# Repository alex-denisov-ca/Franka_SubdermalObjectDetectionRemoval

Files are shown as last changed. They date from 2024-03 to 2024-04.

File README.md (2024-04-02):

# Robot-assisted Subdermal Foreign Object Detection and Removal For Franka Panda

## **Quick Start Guide**
This project is for use with the Franka Emika Panda cobot and the Healson C30L ultrasound probe, as well as similar probes and cobots.

The project uses the Franka robot alongside an ultrasound probe to scan a section of ultrasound gel or water; the medium will mimic human flesh. Within the medium, one or more metallic bolts or other objects will simulate shrapnel subdermally embedded. 

*(0): Startup*<br />
Git clone and build the project, specifically the csc496 directory of the project in the same directory that contains the Franka Panda's [libfranka](https://github.com/frankaemika/libfranka) directory.

Connect to the Franka control interface and ensure everything is properly initialized; joints are unlocked, and the robot is not reflex-locked or user-stopped.
First, set the z component of the end effector to 150mm in Franka Desk, also measure and set the weight of the Franka hand including the probe, grippers and holders (print and user depedant).
Second, enable the [FCI](https://frankaemika.github.io/docs/getting_started.html)

Install printed hardware to the Franka hand, seal important electrical components on and around the robot, set your tray/working area, then fill the tray with the preferred medium and insert foreign bodies.

Then start the docker container included in the "docker" directory within "csc496":
    run build_docker_container.sh
    run start_docker_container.sh
    run open_docker_terminal.sh
    to close the running terminal, run stop_docker_container.sh

*(1): Running the code*<br />
Inside the docker container, go to `/root/git/scratchpad/csc496/build` and run `rm CMakeCache.txt && cmake ../ && make` in the bash terminal.
then run `run.sh` in the terminal; this script links all the steps together onto a single terminal, follow instructions and prompts that show up on the terminal.
    There will be four distinct steps, with an "operator" sitting at the terminal and the ultrasound screen and a "guide" watching the robot and manning the enabling device.

    (0): Setting the origin of the scanner
        - The guide will move the probe to the bottom left of the tray farthest away from the robot
           and to the side that it has its power ports.

    (1): Rough scanning mode
        - the probe will begin scanning the working area, the operator should press space 
          when an anomaly is detected.

    (2): Keyboard guidance mode
        - The operator will have to navigate to the rough position and center the object on the ultrasound, 
          this should be done with the help of the guide to avoid collisions.

    (2.5): (Suggested) Remove the ultrasound probe from the holder.      

    (3): Object Retrieval
        - after the operator has identified the object then, the robot will attempt to grasp the object, 
          upon completion, it will home and drop the object for the guide to catch upon operator approval. 

## **Running Details**
if, for some reason, you don't use `run.sh`, then you can run each step individually after following the initial instructions from Startup, as shown below:<br />

*(0): Set origin of scan*<br />
     - sets and records the origin of scanning sequence<br />
     - use for manually running scan from origin<br />

    Run manually:
        ./set_origin <YOUR_FRANKA_IP>

    Controls:
        Enter - saves the position
        Any other key - quit the program

*(1): Automated scanning of the medium in a rectangular pattern*<br />
     - when the operator sees a foreign object on the ultrasound screen they press the space bar<br />
     - the location is saved in a text file for further inspection and adjustment<br />
     - this simulates scanning a large portion of the body to locate multiple pieces of shrapenal<br />

    Run manually:
        ./run_autoscan_rough_capture <YOUR_FRANKA_IP> <Origin X> <Origin Y> <Origin Z>

    Controls:
        Space - saves the position

*(2): Fine position finding* <br />
     - Now that you know the approximate position of the shrapnel, use the keyboard to locate it <br />
     - Once the operator has found the center of the object, they will press 'space' and save the coordinates <br />
     - The saved coordinates will also be saved to a text file; both to handle multiple pieces of shrapnel, or multiple grasping attempts of the same object <br />
    
    Run:
        ./run_keyboard_input_capture <YOUR_FRANKA_IP>  <X> <Y> <Z>

     Controls:
        W - moves forward (towards the robots base)
        A - moves left (towards the side of the robots power connectors)
        S - moves backward (away from the robots base)
        D - moves right (towards the side of the robots ethernet port)
        Space - saves the position
        R - moves upwards
        F - move downwards
        T - releases/opens the gripper
        G - closes gripper to grasp
        Escape - stops and closes the program

*(3): Object extraction*<br />
     - The user will be prompted for a raw x,y position<br />
     - The operator will enter the x,y positions determined from the previous step<br />
     - The robot will then automatically go to its home position, open the gripper, go to the object, close the gripper, and extract it<br />
     - If the robot fails to grasp and extract the object, repeat step 2 or use alternative object positions already collected in the previous step<br />
     - Press the space bar to open the gripper and drop the extracted object (or simply open the gripper for another iteration)<br />
  
    Run manually:
        ./grasp_given_xyz <YOUR_FRANKA_IP>  <X> <Y> <Z> 
        
    Inputs:
        x position - raw x position of ultrasound detected object
        y position - raw y position of ultrasound detected object

     Controls:
        Enter - On prompt, continue execution of the next task
        Space - On prompt, open the gripper

## **Hardware and Envrionment**
For hardware used in the project, go to the "Models" directory and see [Hardware_Instructions.pdf](https://github.com/alex-denisov-ca/Franka_SubdermalObjectDetectionRemoval/blob/main/Models/Hardware_Instructions.pdf) for printing and assembly information.

Once assembled, there is a distance of 150mm from the flange of the robot to the ends of the grippers; set these values in Franka Desk.
It should also be noted that the center of the ultrasound probe is 60mm away from the center of the end-effector; 
with any tray or working area, there are mechanical limitations that result in spaces where the probe cannot scan / the grippers cannot reach.

It is suggested to use an ultrasound gel for running this project; for best results, smooth the gel before every run (this can be done with something unimportant, like a student ID).

For running in custom environments, you will also have to measure dimensions and the coordinate of your working space; `set_origin` allows you to move the board anywhere in the working space (without rotations), but it may be necessary to manually tweak code if your tray is larger or smaller than the one provided to work with the auto scan feature.

## **Dependencies**
All files are to be run on a Linux real-time kernel.
The github repo OR the csc496 directory included in the repo must be in the same directory as [libfranka](https://github.com/frankaemika/libfranka); i.e in some directory X, there will X/libfranka, X/csc496, X/Models, etc.

If you are NOT running the provided docker container, you will have to have at minimum [ncurses-6.0](https://lists.gnu.org/archive/html/info-gnu/2015-08/msg00002.html) installed; 

## **Citation**
This codebase is modified from the one provided in CSC496H5 at the University of Toronto Mississauga, taught by Professor Lueder Kahrs and provided by Ruthrash Hari; based on the Franka Emika [libfranka repo.](https://github.com/frankaemika/libfranka)

Citation is available in the About section of the GitHub project or the CITATION.cff file.

## **Testing**
We have tested this repo using the Franka Panda robot, the Healson C30L ultrasound probe, and all stl files provided in this repository. Tests have been running on multiple robots; different robots have different vertical offsets from their base due to mounting variances, and thus, some board parameters need to be tweaked between robots.

When testing, running for the first time, or tweaking the parameters, it is important to always have one person manning the enabling device and developing incrementally with one change at a time. For example, changing the speed; start at a known working speed, then increment it to the desired value, etc.

In testing the code, it is best to perform the tests without a medium inside the tray. We have tested each of the four sections above individually and together with `run.sh`. 

We have run through all steps of the project multiple times using a 15mm M6 screw (shrapnel) embedded in ultrasound gel (medium), resulting in successful objection detection at all stages and removal from the medium. 

Our set_origin code works at any point in the working space; it simply records the x,y, and z components of the gripper and saves them to a text file.

We ran our rough scanning code with the tray affixed at different positions on two robots; the scanning code given the set_origin program will adapt to the z offset and work with multiple volumes of the medium. 

We ran keyboard extraction in many envrioments, it may fail if the operator runs the gripper into the wall fo the tray or another rigid object, fine tuning for different application is possible by setting how much the gripper moves on each keypress.

We varied the placement of the shrapnel inside the medium, within the mechanial boundaries of the gripper and where successful in extracting the bolt; the bolt was succesfully picked up in both the laying down and  upright position. Although, some orentiations are untested, such as the bolt laying at a 45 degree angle; making it hard to pick up and easily slide away from the gripper jaws. 

If the program is unsuccessful, there may be times that the terminal running the program will freeze to an orphan thread run by one of the members. It is also important to move the robot between runs to ensure there is no reflex-lock and also to not put excessive force on the robot while it's moving and running.

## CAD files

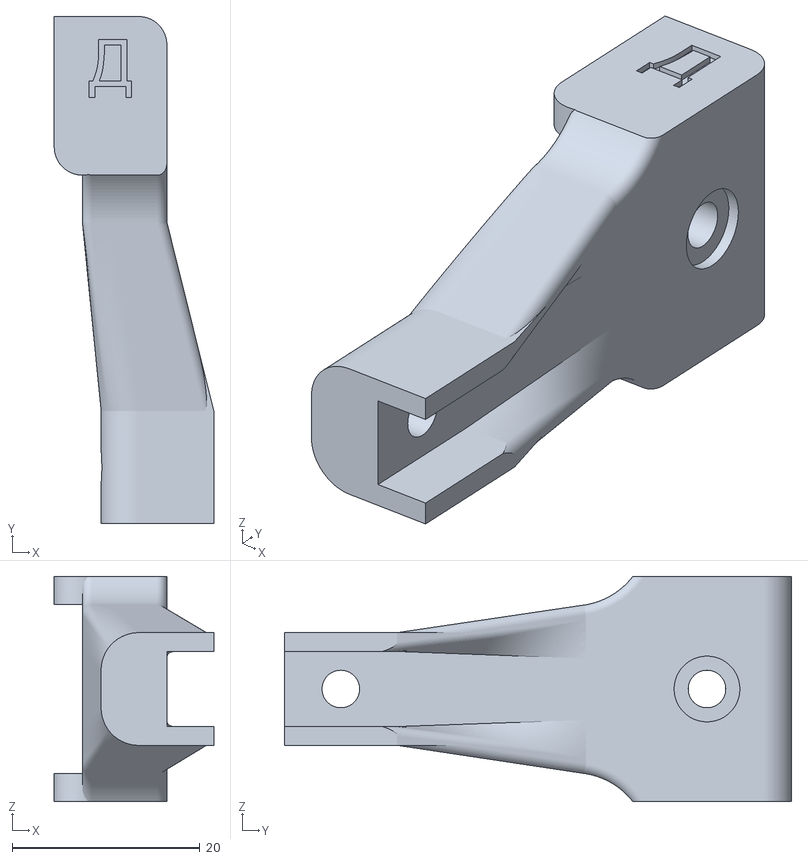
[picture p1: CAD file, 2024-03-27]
Models/Franka_gripper.stl
17.0 x 54.0 x 24.0

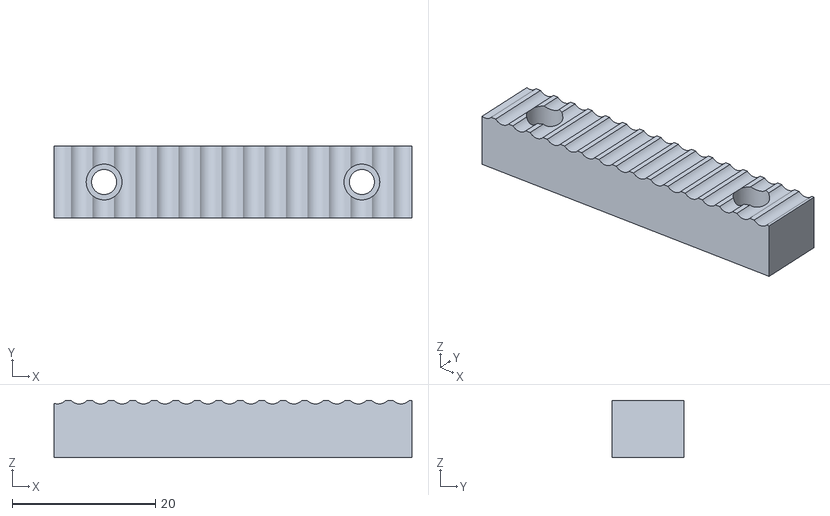
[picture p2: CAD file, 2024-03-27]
Models/Franka_probe_clamp_softjaw.stl
50.0 x 10.0 x 8.00

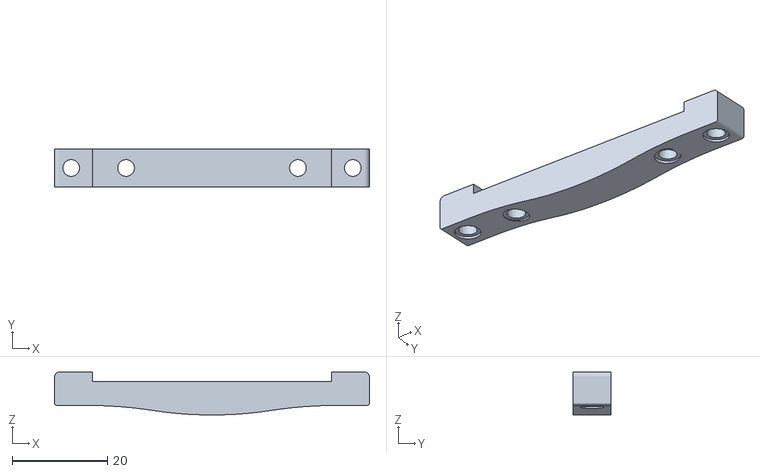
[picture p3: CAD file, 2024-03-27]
Models/Franka_probe_clamp.stl
66.0 x 8.00 x 9.00

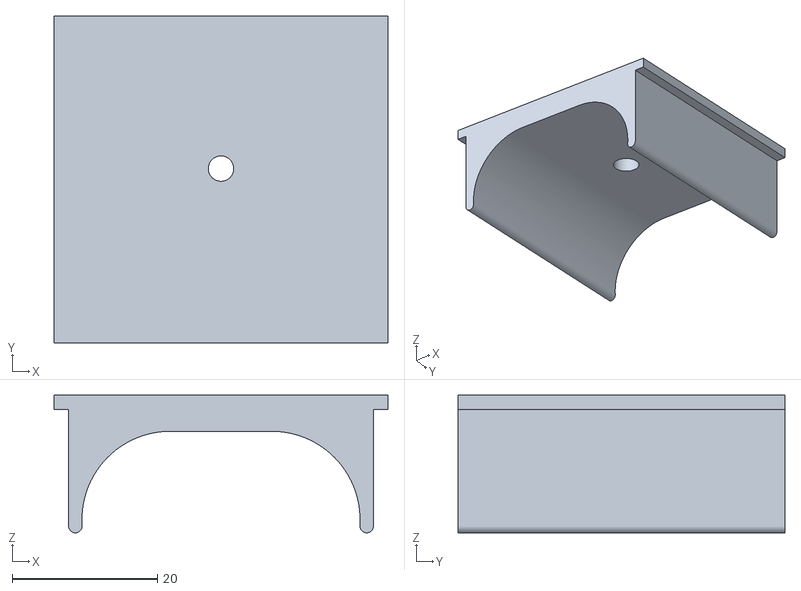
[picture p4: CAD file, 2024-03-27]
Models/Franka_probe_holder_softjaw.stl
46.0 x 45.0 x 19.0

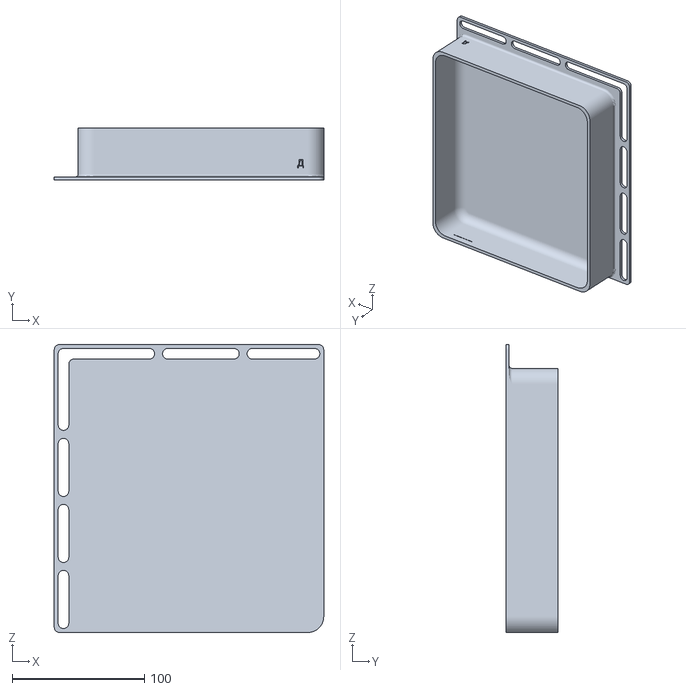
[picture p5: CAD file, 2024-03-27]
Models/Tray_surgery_mock.stl
204.0 x 39.5 x 218.0

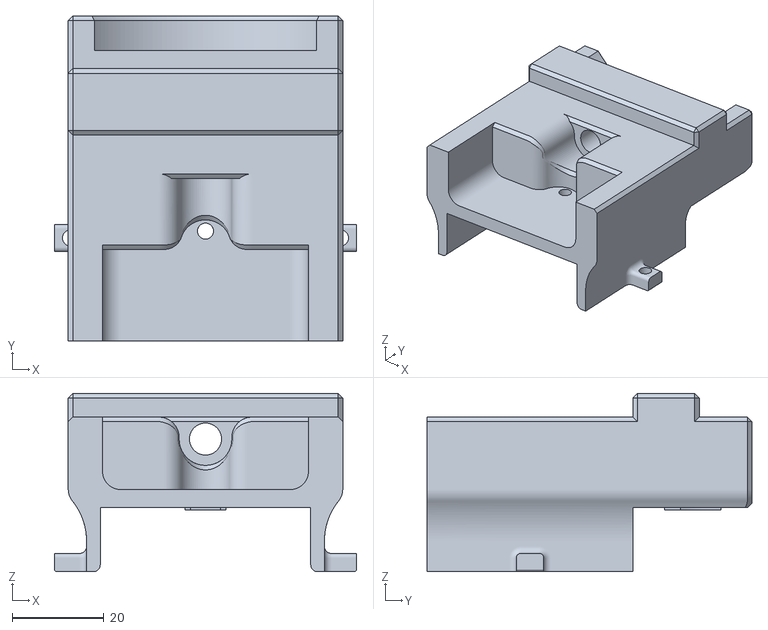
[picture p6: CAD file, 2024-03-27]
Models/Franka_probe_holder.stl
66.0 x 71.0 x 39.0

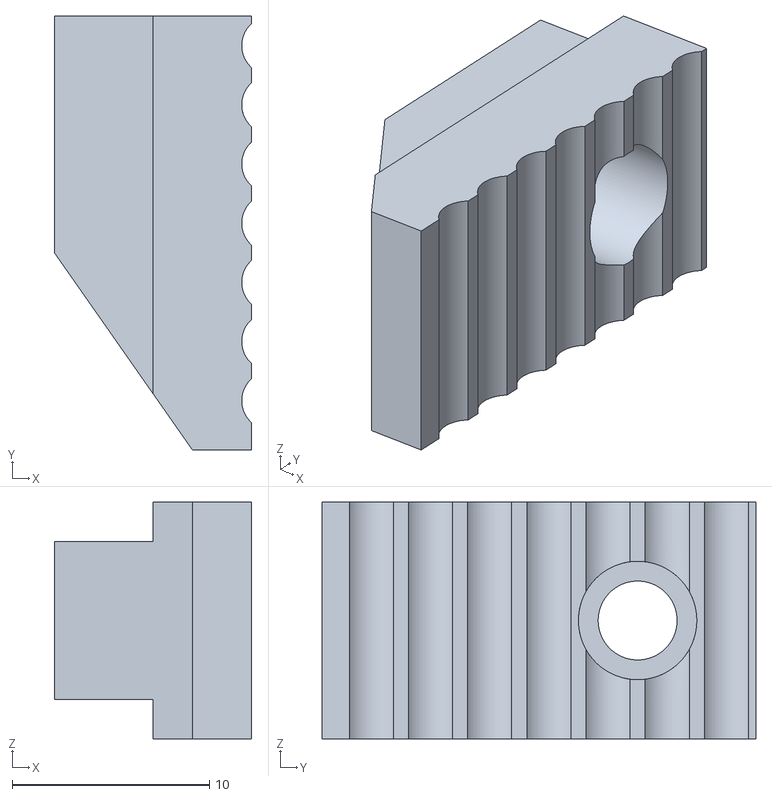
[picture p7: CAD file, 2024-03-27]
Models/Franka_gripper_softjaw.stl
10.0 x 22.0 x 12.0

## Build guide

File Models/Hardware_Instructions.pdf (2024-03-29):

Hardware and 3D Printing Documentation Robot-assisted Subdermal Foreign Object Detection and Removal For Franka Emika Panda & Similar Robots Required Hardware:
1x M6 Bolt - 40mm: attachment of the ultrasound holder to the Franka hand
3x (Optional) M6 Bolt - 10mm: tray fastening depends on mounting surface and tray used

2x M3 Bolt - 45mm: attachment of the clamp to the holder
2x M3 Bolt - 20mm: attachment of the grippers to the end-effector
5x M3 Bolt - 12mm: attachment of malleable materials to rigid bodies

7x M3 Nuts
6x M3 Thumb Nuts - 12x4mm

Printing Instructions:
Objects shown in light green are to be printed in PLA or another suitable material; it is preferable to use tree supports and print with four walls and 20-35 percent infill, depending on the material.

Objects shown in light blue from left to right are Franka_probe_holder.stl, Franka_probe_holder.stl, and (2x) Franka_gripper.stl

Objects shown in yellow/gray stripes are to be printed in a malleable material such as TPU with any shore hardness; preferably print with a brim, no supports, four walls and use Cross3D or similar deformation-compliant infill pattern at 10-25 percent infill.

Objects shown in striped yellow/gray from left to right are: Franka_probe_softjaw.stl, Franka_probe_holder_softjaw.stl and (2x) Franka_gripper_softjaw.stl

Below is the suggested printed orientation for each object:

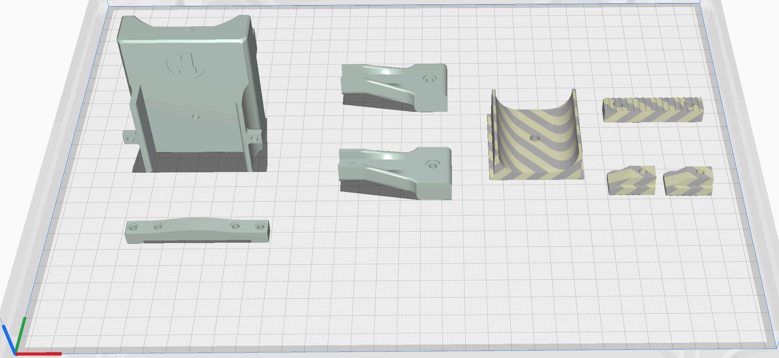
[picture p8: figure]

For Franka Emika Panda & Similar Robots

You may use the tray provided as Tray_surgery_mock.stl to hold ultrasound gel/liquid for the surgery mock; any other rigid pan or tray will also work, but it must be fastened and waterproofed correctly.

The figure below shows the orientation for printing Tray_surgery_mock.stl; use an attachment glue as large flat square objects will warp when cooling for most materials. Print in PLA or another suitable material; no supports are needed, and print with six walls and 20-35 percent infill, depending on the material. Use as large of a skirt as possible when printing.

The Tray used in this project is quite large and may not be suitable for all users depending on printer limitations; users should scale the mock or use an alternative method to hold the gel/water and shrapnel.

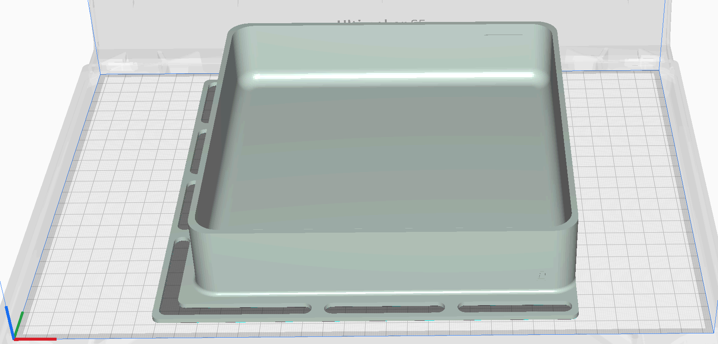
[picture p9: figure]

Assembly:
Use 12mm M3 bolts to attach all TPU parts to rigid parts, with bolts.
Use the 20mm M3 bolts and the thumb screws to attach the grippers to the flange extenders.
Use the 45mm M3 bolts to attach the clamp to the ultrasound holder, alongside two bolts and four thumb screws.
Use the 40mm M6 bolt to attach the probe holder to the Franka Panda robot.

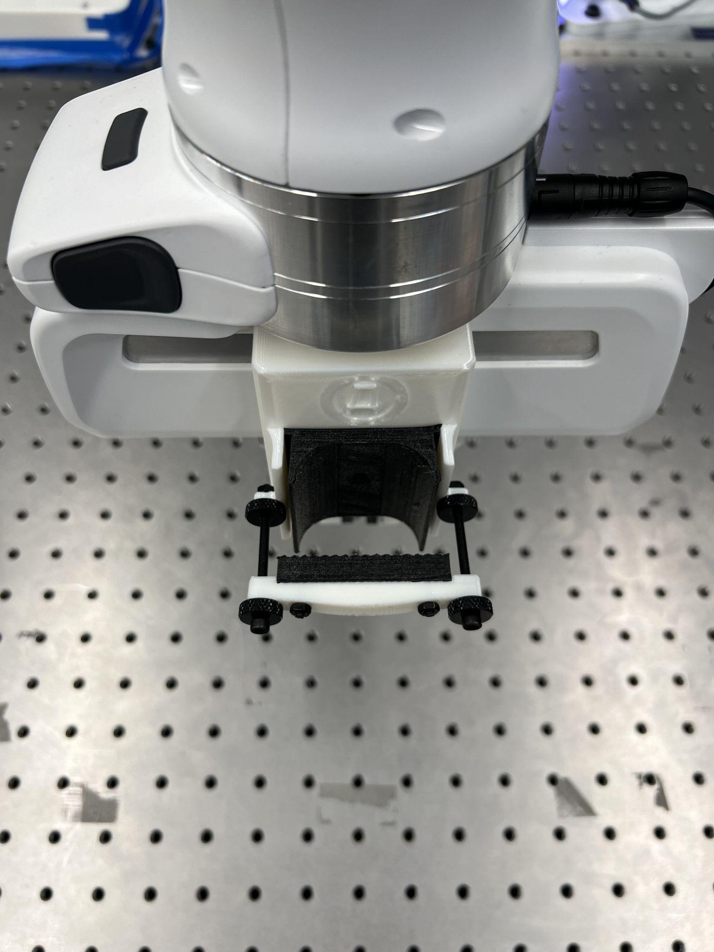
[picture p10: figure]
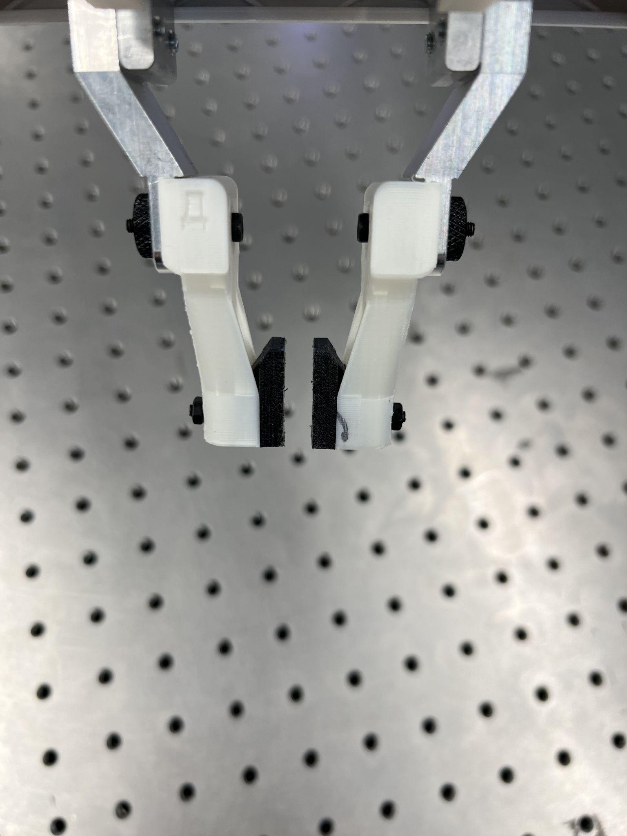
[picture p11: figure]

For Franka Emika Panda & Similar Robots

Photos of assembled components are provided below:

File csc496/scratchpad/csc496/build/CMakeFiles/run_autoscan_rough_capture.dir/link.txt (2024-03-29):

/usr/bin/c++     CMakeFiles/run_autoscan_rough_capture.dir/runners/autoscan_rough_capture.cpp.o CMakeFiles/run_autoscan_rough_capture.dir/src/common.cpp.o CMakeFiles/run_autoscan_rough_capture.dir/src/ik.cpp.o CMakeFiles/run_autoscan_rough_capture.dir/src/teleop/follower.cpp.o CMakeFiles/run_autoscan_rough_capture.dir/src/teleop/leader.cpp.o CMakeFiles/run_autoscan_rough_capture.dir/src/teleop/network_client.cpp.o CMakeFiles/run_autoscan_rough_capture.dir/src/teleop/network_server.cpp.o  -o run_autoscan_rough_capture   -L/usr/local/include  -Wl,-rpath,/usr/local/include:/usr/local/lib /usr/local/lib/libfranka.so.0.9.2 /usr/lib/x86_64-linux-gnu/libboost_system.so.1.71.0 /usr/lib/x86_64-linux-gnu/libboost_thread.so.1.71.0 /usr/lib/x86_64-linux-gnu/libPocoFoundation.so.62 -lcurses /usr/lib/x86_64-linux-gnu/libform.so -lpthread -ldl -lrt /usr/lib/x86_64-linux-gnu/libpcre.so /usr/lib/x86_64-linux-gnu/libz.so /usr/lib/x86_64-linux-gnu/libboost_atomic.so.1.71.0 -pthread

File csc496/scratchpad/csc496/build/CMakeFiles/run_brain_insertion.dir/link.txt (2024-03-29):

/usr/bin/c++     CMakeFiles/run_brain_insertion.dir/runners/brain_insertion.cpp.o CMakeFiles/run_brain_insertion.dir/src/common.cpp.o CMakeFiles/run_brain_insertion.dir/src/ik.cpp.o CMakeFiles/run_brain_insertion.dir/src/teleop/follower.cpp.o CMakeFiles/run_brain_insertion.dir/src/teleop/leader.cpp.o CMakeFiles/run_brain_insertion.dir/src/teleop/network_client.cpp.o CMakeFiles/run_brain_insertion.dir/src/teleop/network_server.cpp.o  -o run_brain_insertion   -L/usr/local/include  -Wl,-rpath,/usr/local/include:/usr/local/lib /usr/local/lib/libfranka.so.0.9.2 /usr/lib/x86_64-linux-gnu/libboost_system.so.1.71.0 /usr/lib/x86_64-linux-gnu/libboost_thread.so.1.71.0 /usr/lib/x86_64-linux-gnu/libPocoFoundation.so.62 -lpthread -ldl -lrt /usr/lib/x86_64-linux-gnu/libpcre.so /usr/lib/x86_64-linux-gnu/libz.so /usr/lib/x86_64-linux-gnu/libboost_atomic.so.1.71.0 -pthread

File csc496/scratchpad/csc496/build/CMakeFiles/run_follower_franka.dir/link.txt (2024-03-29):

/usr/bin/c++     CMakeFiles/run_follower_franka.dir/runners/teleop/follower_franka.cpp.o  -o run_follower_franka   -L/usr/local/include  -Wl,-rpath,/usr/local/include:/usr/local/lib libfollower.a libnetwork_server.a libfranka_common.a libik.a /usr/local/lib/libfranka.so.0.9.2 /usr/lib/x86_64-linux-gnu/libboost_system.so.1.71.0 /usr/lib/x86_64-linux-gnu/libboost_thread.so.1.71.0 /usr/lib/x86_64-linux-gnu/libboost_atomic.so.1.71.0 -pthread

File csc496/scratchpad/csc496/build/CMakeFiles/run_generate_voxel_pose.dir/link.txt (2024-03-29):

/usr/bin/c++     CMakeFiles/run_generate_voxel_pose.dir/runners/generate_voxel_pose.cpp.o CMakeFiles/run_generate_voxel_pose.dir/src/common.cpp.o CMakeFiles/run_generate_voxel_pose.dir/src/ik.cpp.o CMakeFiles/run_generate_voxel_pose.dir/src/teleop/follower.cpp.o CMakeFiles/run_generate_voxel_pose.dir/src/teleop/leader.cpp.o CMakeFiles/run_generate_voxel_pose.dir/src/teleop/network_client.cpp.o CMakeFiles/run_generate_voxel_pose.dir/src/teleop/network_server.cpp.o  -o run_generate_voxel_pose   -L/usr/local/include  -Wl,-rpath,/usr/local/include:/usr/local/lib /usr/local/lib/libfranka.so.0.9.2 /usr/lib/x86_64-linux-gnu/libboost_system.so.1.71.0 /usr/lib/x86_64-linux-gnu/libboost_thread.so.1.71.0 /usr/lib/x86_64-linux-gnu/libPocoFoundation.so.62 -lpthread -ldl -lrt /usr/lib/x86_64-linux-gnu/libpcre.so /usr/lib/x86_64-linux-gnu/libz.so /usr/lib/x86_64-linux-gnu/libboost_atomic.so.1.71.0 -pthread

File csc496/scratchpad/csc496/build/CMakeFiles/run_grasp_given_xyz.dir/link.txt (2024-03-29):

/usr/bin/c++     CMakeFiles/run_grasp_given_xyz.dir/runners/grasp_given_xyz.cpp.o CMakeFiles/run_grasp_given_xyz.dir/src/common.cpp.o CMakeFiles/run_grasp_given_xyz.dir/src/ik.cpp.o CMakeFiles/run_grasp_given_xyz.dir/src/teleop/follower.cpp.o CMakeFiles/run_grasp_given_xyz.dir/src/teleop/leader.cpp.o CMakeFiles/run_grasp_given_xyz.dir/src/teleop/network_client.cpp.o CMakeFiles/run_grasp_given_xyz.dir/src/teleop/network_server.cpp.o  -o run_grasp_given_xyz   -L/usr/local/include  -Wl,-rpath,/usr/local/include:/usr/local/lib /usr/local/lib/libfranka.so.0.9.2 /usr/lib/x86_64-linux-gnu/libboost_system.so.1.71.0 /usr/lib/x86_64-linux-gnu/libboost_thread.so.1.71.0 /usr/lib/x86_64-linux-gnu/libPocoFoundation.so.62 -lcurses /usr/lib/x86_64-linux-gnu/libform.so -lpthread -ldl -lrt /usr/lib/x86_64-linux-gnu/libpcre.so /usr/lib/x86_64-linux-gnu/libz.so /usr/lib/x86_64-linux-gnu/libboost_atomic.so.1.71.0 -pthread

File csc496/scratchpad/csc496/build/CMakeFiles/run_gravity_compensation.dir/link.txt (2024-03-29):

/usr/bin/c++     CMakeFiles/run_gravity_compensation.dir/runners/gravity_compensation.cpp.o CMakeFiles/run_gravity_compensation.dir/src/common.cpp.o CMakeFiles/run_gravity_compensation.dir/src/ik.cpp.o CMakeFiles/run_gravity_compensation.dir/src/teleop/follower.cpp.o CMakeFiles/run_gravity_compensation.dir/src/teleop/leader.cpp.o CMakeFiles/run_gravity_compensation.dir/src/teleop/network_client.cpp.o CMakeFiles/run_gravity_compensation.dir/src/teleop/network_server.cpp.o  -o run_gravity_compensation   -L/usr/local/include  -Wl,-rpath,/usr/local/include:/usr/local/lib /usr/local/lib/libfranka.so.0.9.2 /usr/lib/x86_64-linux-gnu/libboost_system.so.1.71.0 /usr/lib/x86_64-linux-gnu/libboost_thread.so.1.71.0 /usr/lib/x86_64-linux-gnu/libPocoFoundation.so.62 -lpthread -ldl -lrt /usr/lib/x86_64-linux-gnu/libpcre.so /usr/lib/x86_64-linux-gnu/libz.so /usr/lib/x86_64-linux-gnu/libboost_atomic.so.1.71.0 -pthread

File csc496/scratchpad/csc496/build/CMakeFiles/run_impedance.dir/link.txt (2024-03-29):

/usr/bin/c++     CMakeFiles/run_impedance.dir/runners/impedance.cpp.o CMakeFiles/run_impedance.dir/src/common.cpp.o CMakeFiles/run_impedance.dir/src/ik.cpp.o CMakeFiles/run_impedance.dir/src/teleop/follower.cpp.o CMakeFiles/run_impedance.dir/src/teleop/leader.cpp.o CMakeFiles/run_impedance.dir/src/teleop/network_client.cpp.o CMakeFiles/run_impedance.dir/src/teleop/network_server.cpp.o  -o run_impedance   -L/usr/local/include  -Wl,-rpath,/usr/local/include:/usr/local/lib /usr/local/lib/libfranka.so.0.9.2 /usr/lib/x86_64-linux-gnu/libboost_system.so.1.71.0 /usr/lib/x86_64-linux-gnu/libboost_thread.so.1.71.0 /usr/lib/x86_64-linux-gnu/libPocoFoundation.so.62 -lpthread -ldl -lrt /usr/lib/x86_64-linux-gnu/libpcre.so /usr/lib/x86_64-linux-gnu/libz.so /usr/lib/x86_64-linux-gnu/libboost_atomic.so.1.71.0 -pthread

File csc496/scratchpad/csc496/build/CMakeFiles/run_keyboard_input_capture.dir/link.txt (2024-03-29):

/usr/bin/c++     CMakeFiles/run_keyboard_input_capture.dir/runners/keyboard_input_capture.cpp.o CMakeFiles/run_keyboard_input_capture.dir/src/common.cpp.o CMakeFiles/run_keyboard_input_capture.dir/src/ik.cpp.o CMakeFiles/run_keyboard_input_capture.dir/src/teleop/follower.cpp.o CMakeFiles/run_keyboard_input_capture.dir/src/teleop/leader.cpp.o CMakeFiles/run_keyboard_input_capture.dir/src/teleop/network_client.cpp.o CMakeFiles/run_keyboard_input_capture.dir/src/teleop/network_server.cpp.o  -o run_keyboard_input_capture   -L/usr/local/include  -Wl,-rpath,/usr/local/include:/usr/local/lib /usr/local/lib/libfranka.so.0.9.2 /usr/lib/x86_64-linux-gnu/libboost_system.so.1.71.0 /usr/lib/x86_64-linux-gnu/libboost_thread.so.1.71.0 /usr/lib/x86_64-linux-gnu/libPocoFoundation.so.62 -lcurses /usr/lib/x86_64-linux-gnu/libform.so -lpthread -ldl -lrt /usr/lib/x86_64-linux-gnu/libpcre.so /usr/lib/x86_64-linux-gnu/libz.so /usr/lib/x86_64-linux-gnu/libboost_atomic.so.1.71.0 -pthread

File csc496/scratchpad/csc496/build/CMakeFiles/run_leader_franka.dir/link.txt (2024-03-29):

/usr/bin/c++     CMakeFiles/run_leader_franka.dir/runners/teleop/leader_franka.cpp.o  -o run_leader_franka   -L/usr/local/include  -Wl,-rpath,/usr/local/include:/usr/local/lib libleader.a libnetwork_client.a libfranka_common.a /usr/local/lib/libfranka.so.0.9.2 /usr/lib/x86_64-linux-gnu/libboost_system.so.1.71.0 /usr/lib/x86_64-linux-gnu/libboost_thread.so.1.71.0 /usr/lib/x86_64-linux-gnu/libboost_atomic.so.1.71.0 -pthread

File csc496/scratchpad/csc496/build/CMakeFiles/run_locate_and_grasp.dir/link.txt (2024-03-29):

/usr/bin/c++     CMakeFiles/run_locate_and_grasp.dir/runners/locate_and_grasp.cpp.o CMakeFiles/run_locate_and_grasp.dir/src/common.cpp.o CMakeFiles/run_locate_and_grasp.dir/src/ik.cpp.o CMakeFiles/run_locate_and_grasp.dir/src/teleop/follower.cpp.o CMakeFiles/run_locate_and_grasp.dir/src/teleop/leader.cpp.o CMakeFiles/run_locate_and_grasp.dir/src/teleop/network_client.cpp.o CMakeFiles/run_locate_and_grasp.dir/src/teleop/network_server.cpp.o  -o run_locate_and_grasp   -L/usr/local/include  -Wl,-rpath,/usr/local/include:/usr/local/lib /usr/local/lib/libfranka.so.0.9.2 /usr/lib/x86_64-linux-gnu/libboost_system.so.1.71.0 /usr/lib/x86_64-linux-gnu/libboost_thread.so.1.71.0 /usr/lib/x86_64-linux-gnu/libPocoFoundation.so.62 -lcurses /usr/lib/x86_64-linux-gnu/libform.so -lpthread -ldl -lrt /usr/lib/x86_64-linux-gnu/libpcre.so /usr/lib/x86_64-linux-gnu/libz.so /usr/lib/x86_64-linux-gnu/libboost_atomic.so.1.71.0 -pthread

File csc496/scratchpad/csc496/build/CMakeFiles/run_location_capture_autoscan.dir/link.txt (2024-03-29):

/usr/bin/c++     CMakeFiles/run_location_capture_autoscan.dir/runners/location_capture_autoscan.cpp.o CMakeFiles/run_location_capture_autoscan.dir/src/common.cpp.o CMakeFiles/run_location_capture_autoscan.dir/src/ik.cpp.o CMakeFiles/run_location_capture_autoscan.dir/src/teleop/follower.cpp.o CMakeFiles/run_location_capture_autoscan.dir/src/teleop/leader.cpp.o CMakeFiles/run_location_capture_autoscan.dir/src/teleop/network_client.cpp.o CMakeFiles/run_location_capture_autoscan.dir/src/teleop/network_server.cpp.o  -o run_location_capture_autoscan   -L/usr/local/include  -Wl,-rpath,/usr/local/include:/usr/local/lib /usr/local/lib/libfranka.so.0.9.2 /usr/lib/x86_64-linux-gnu/libboost_system.so.1.71.0 /usr/lib/x86_64-linux-gnu/libboost_thread.so.1.71.0 /usr/lib/x86_64-linux-gnu/libPocoFoundation.so.62 -lcurses /usr/lib/x86_64-linux-gnu/libform.so -lpthread -ldl -lrt /usr/lib/x86_64-linux-gnu/libpcre.so /usr/lib/x86_64-linux-gnu/libz.so /usr/lib/x86_64-linux-gnu/libboost_atomic.so.1.71.0 -pthread

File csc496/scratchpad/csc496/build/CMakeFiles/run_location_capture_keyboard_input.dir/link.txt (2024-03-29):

/usr/bin/c++     CMakeFiles/run_location_capture_keyboard_input.dir/runners/location_capture_keyboard_input.cpp.o CMakeFiles/run_location_capture_keyboard_input.dir/src/common.cpp.o CMakeFiles/run_location_capture_keyboard_input.dir/src/ik.cpp.o CMakeFiles/run_location_capture_keyboard_input.dir/src/teleop/follower.cpp.o CMakeFiles/run_location_capture_keyboard_input.dir/src/teleop/leader.cpp.o CMakeFiles/run_location_capture_keyboard_input.dir/src/teleop/network_client.cpp.o CMakeFiles/run_location_capture_keyboard_input.dir/src/teleop/network_server.cpp.o  -o run_location_capture_keyboard_input   -L/usr/local/include  -Wl,-rpath,/usr/local/include:/usr/local/lib /usr/local/lib/libfranka.so.0.9.2 /usr/lib/x86_64-linux-gnu/libboost_system.so.1.71.0 /usr/lib/x86_64-linux-gnu/libboost_thread.so.1.71.0 /usr/lib/x86_64-linux-gnu/libPocoFoundation.so.62 -lcurses /usr/lib/x86_64-linux-gnu/libform.so -lpthread -ldl -lrt /usr/lib/x86_64-linux-gnu/libpcre.so /usr/lib/x86_64-linux-gnu/libz.so /usr/lib/x86_64-linux-gnu/libboost_atomic.so.1.71.0 -pthread

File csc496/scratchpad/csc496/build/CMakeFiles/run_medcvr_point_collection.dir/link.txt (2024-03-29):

/usr/bin/c++     CMakeFiles/run_medcvr_point_collection.dir/runners/medcvr_point_collection.cpp.o CMakeFiles/run_medcvr_point_collection.dir/src/common.cpp.o CMakeFiles/run_medcvr_point_collection.dir/src/ik.cpp.o CMakeFiles/run_medcvr_point_collection.dir/src/teleop/follower.cpp.o CMakeFiles/run_medcvr_point_collection.dir/src/teleop/leader.cpp.o CMakeFiles/run_medcvr_point_collection.dir/src/teleop/network_client.cpp.o CMakeFiles/run_medcvr_point_collection.dir/src/teleop/network_server.cpp.o  -o run_medcvr_point_collection   -L/usr/local/include  -Wl,-rpath,/usr/local/include:/usr/local/lib /usr/local/lib/libfranka.so.0.9.2 /usr/lib/x86_64-linux-gnu/libboost_system.so.1.71.0 /usr/lib/x86_64-linux-gnu/libboost_thread.so.1.71.0 /usr/lib/x86_64-linux-gnu/libPocoFoundation.so.62 -lpthread -ldl -lrt /usr/lib/x86_64-linux-gnu/libpcre.so /usr/lib/x86_64-linux-gnu/libz.so /usr/lib/x86_64-linux-gnu/libboost_atomic.so.1.71.0 -pthread

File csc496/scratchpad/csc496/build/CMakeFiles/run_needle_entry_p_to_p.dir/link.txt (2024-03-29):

/usr/bin/c++     CMakeFiles/run_needle_entry_p_to_p.dir/runners/needle_entry_p_to_p.cpp.o CMakeFiles/run_needle_entry_p_to_p.dir/src/common.cpp.o CMakeFiles/run_needle_entry_p_to_p.dir/src/ik.cpp.o CMakeFiles/run_needle_entry_p_to_p.dir/src/teleop/follower.cpp.o CMakeFiles/run_needle_entry_p_to_p.dir/src/teleop/leader.cpp.o CMakeFiles/run_needle_entry_p_to_p.dir/src/teleop/network_client.cpp.o CMakeFiles/run_needle_entry_p_to_p.dir/src/teleop/network_server.cpp.o  -o run_needle_entry_p_to_p   -L/usr/local/include  -Wl,-rpath,/usr/local/include:/usr/local/lib /usr/local/lib/libfranka.so.0.9.2 /usr/lib/x86_64-linux-gnu/libboost_system.so.1.71.0 /usr/lib/x86_64-linux-gnu/libboost_thread.so.1.71.0 /usr/lib/x86_64-linux-gnu/libPocoFoundation.so.62 -lpthread -ldl -lrt /usr/lib/x86_64-linux-gnu/libpcre.so /usr/lib/x86_64-linux-gnu/libz.so /usr/lib/x86_64-linux-gnu/libboost_atomic.so.1.71.0 -pthread

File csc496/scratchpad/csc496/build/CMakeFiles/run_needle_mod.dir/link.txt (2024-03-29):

/usr/bin/c++     CMakeFiles/run_needle_mod.dir/runners/needle_mod.cpp.o CMakeFiles/run_needle_mod.dir/src/common.cpp.o CMakeFiles/run_needle_mod.dir/src/ik.cpp.o CMakeFiles/run_needle_mod.dir/src/teleop/follower.cpp.o CMakeFiles/run_needle_mod.dir/src/teleop/leader.cpp.o CMakeFiles/run_needle_mod.dir/src/teleop/network_client.cpp.o CMakeFiles/run_needle_mod.dir/src/teleop/network_server.cpp.o  -o run_needle_mod   -L/usr/local/include  -Wl,-rpath,/usr/local/include:/usr/local/lib /usr/lib/x86_64-linux-gnu/libboost_system.so.1.71.0 /usr/lib/x86_64-linux-gnu/libboost_thread.so.1.71.0 /usr/local/lib/libfranka.so.0.9.2 -lncurses /usr/lib/x86_64-linux-gnu/libPocoFoundation.so.62 -lpthread -ldl -lrt /usr/lib/x86_64-linux-gnu/libpcre.so /usr/lib/x86_64-linux-gnu/libz.so /usr/lib/x86_64-linux-gnu/libboost_atomic.so.1.71.0 -pthread

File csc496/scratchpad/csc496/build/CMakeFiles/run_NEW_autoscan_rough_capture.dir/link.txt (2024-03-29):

/usr/bin/c++     CMakeFiles/run_NEW_autoscan_rough_capture.dir/runners/NEW_autoscan_rough_capture.cpp.o CMakeFiles/run_NEW_autoscan_rough_capture.dir/src/common.cpp.o CMakeFiles/run_NEW_autoscan_rough_capture.dir/src/ik.cpp.o CMakeFiles/run_NEW_autoscan_rough_capture.dir/src/teleop/follower.cpp.o CMakeFiles/run_NEW_autoscan_rough_capture.dir/src/teleop/leader.cpp.o CMakeFiles/run_NEW_autoscan_rough_capture.dir/src/teleop/network_client.cpp.o CMakeFiles/run_NEW_autoscan_rough_capture.dir/src/teleop/network_server.cpp.o  -o run_NEW_autoscan_rough_capture   -L/usr/local/include  -Wl,-rpath,/usr/local/include:/usr/local/lib /usr/local/lib/libfranka.so.0.9.2 /usr/lib/x86_64-linux-gnu/libboost_system.so.1.71.0 /usr/lib/x86_64-linux-gnu/libboost_thread.so.1.71.0 /usr/lib/x86_64-linux-gnu/libPocoFoundation.so.62 -lcurses /usr/lib/x86_64-linux-gnu/libform.so -lpthread -ldl -lrt /usr/lib/x86_64-linux-gnu/libpcre.so /usr/lib/x86_64-linux-gnu/libz.so /usr/lib/x86_64-linux-gnu/libboost_atomic.so.1.71.0 -pthread

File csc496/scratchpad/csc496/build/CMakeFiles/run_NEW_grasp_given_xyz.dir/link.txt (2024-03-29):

/usr/bin/c++     CMakeFiles/run_NEW_grasp_given_xyz.dir/runners/NEW_grasp_given_xyz.cpp.o CMakeFiles/run_NEW_grasp_given_xyz.dir/src/common.cpp.o CMakeFiles/run_NEW_grasp_given_xyz.dir/src/ik.cpp.o CMakeFiles/run_NEW_grasp_given_xyz.dir/src/teleop/follower.cpp.o CMakeFiles/run_NEW_grasp_given_xyz.dir/src/teleop/leader.cpp.o CMakeFiles/run_NEW_grasp_given_xyz.dir/src/teleop/network_client.cpp.o CMakeFiles/run_NEW_grasp_given_xyz.dir/src/teleop/network_server.cpp.o  -o run_NEW_grasp_given_xyz   -L/usr/local/include  -Wl,-rpath,/usr/local/include:/usr/local/lib /usr/local/lib/libfranka.so.0.9.2 /usr/lib/x86_64-linux-gnu/libboost_system.so.1.71.0 /usr/lib/x86_64-linux-gnu/libboost_thread.so.1.71.0 /usr/lib/x86_64-linux-gnu/libPocoFoundation.so.62 -lcurses /usr/lib/x86_64-linux-gnu/libform.so -lpthread -ldl -lrt /usr/lib/x86_64-linux-gnu/libpcre.so /usr/lib/x86_64-linux-gnu/libz.so /usr/lib/x86_64-linux-gnu/libboost_atomic.so.1.71.0 -pthread

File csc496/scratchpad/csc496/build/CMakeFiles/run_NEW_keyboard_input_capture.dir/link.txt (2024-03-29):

/usr/bin/c++     CMakeFiles/run_NEW_keyboard_input_capture.dir/runners/NEW_keyboard_input_capture.cpp.o CMakeFiles/run_NEW_keyboard_input_capture.dir/src/common.cpp.o CMakeFiles/run_NEW_keyboard_input_capture.dir/src/ik.cpp.o CMakeFiles/run_NEW_keyboard_input_capture.dir/src/teleop/follower.cpp.o CMakeFiles/run_NEW_keyboard_input_capture.dir/src/teleop/leader.cpp.o CMakeFiles/run_NEW_keyboard_input_capture.dir/src/teleop/network_client.cpp.o CMakeFiles/run_NEW_keyboard_input_capture.dir/src/teleop/network_server.cpp.o  -o run_NEW_keyboard_input_capture   -L/usr/local/include  -Wl,-rpath,/usr/local/include:/usr/local/lib /usr/local/lib/libfranka.so.0.9.2 /usr/lib/x86_64-linux-gnu/libboost_system.so.1.71.0 /usr/lib/x86_64-linux-gnu/libboost_thread.so.1.71.0 /usr/lib/x86_64-linux-gnu/libPocoFoundation.so.62 -lcurses /usr/lib/x86_64-linux-gnu/libform.so -lpthread -ldl -lrt /usr/lib/x86_64-linux-gnu/libpcre.so /usr/lib/x86_64-linux-gnu/libz.so /usr/lib/x86_64-linux-gnu/libboost_atomic.so.1.71.0 -pthread

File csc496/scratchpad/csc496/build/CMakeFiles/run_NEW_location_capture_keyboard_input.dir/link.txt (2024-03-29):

/usr/bin/c++     CMakeFiles/run_NEW_location_capture_keyboard_input.dir/runners/NEW_location_capture_keyboard_input.cpp.o CMakeFiles/run_NEW_location_capture_keyboard_input.dir/src/common.cpp.o CMakeFiles/run_NEW_location_capture_keyboard_input.dir/src/ik.cpp.o CMakeFiles/run_NEW_location_capture_keyboard_input.dir/src/teleop/follower.cpp.o CMakeFiles/run_NEW_location_capture_keyboard_input.dir/src/teleop/leader.cpp.o CMakeFiles/run_NEW_location_capture_keyboard_input.dir/src/teleop/network_client.cpp.o CMakeFiles/run_NEW_location_capture_keyboard_input.dir/src/teleop/network_server.cpp.o  -o run_NEW_location_capture_keyboard_input   -L/usr/local/include  -Wl,-rpath,/usr/local/include:/usr/local/lib /usr/local/lib/libfranka.so.0.9.2 /usr/lib/x86_64-linux-gnu/libboost_system.so.1.71.0 /usr/lib/x86_64-linux-gnu/libboost_thread.so.1.71.0 /usr/lib/x86_64-linux-gnu/libPocoFoundation.so.62 -lcurses /usr/lib/x86_64-linux-gnu/libform.so -lpthread -ldl -lrt /usr/lib/x86_64-linux-gnu/libpcre.so /usr/lib/x86_64-linux-gnu/libz.so /usr/lib/x86_64-linux-gnu/libboost_atomic.so.1.71.0 -pthread

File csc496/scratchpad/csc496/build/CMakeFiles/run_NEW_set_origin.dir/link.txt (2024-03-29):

/usr/bin/c++     CMakeFiles/run_NEW_set_origin.dir/runners/NEW_set_origin.cpp.o CMakeFiles/run_NEW_set_origin.dir/src/common.cpp.o CMakeFiles/run_NEW_set_origin.dir/src/ik.cpp.o CMakeFiles/run_NEW_set_origin.dir/src/teleop/follower.cpp.o CMakeFiles/run_NEW_set_origin.dir/src/teleop/leader.cpp.o CMakeFiles/run_NEW_set_origin.dir/src/teleop/network_client.cpp.o CMakeFiles/run_NEW_set_origin.dir/src/teleop/network_server.cpp.o  -o run_NEW_set_origin   -L/usr/local/include  -Wl,-rpath,/usr/local/include:/usr/local/lib /usr/local/lib/libfranka.so.0.9.2 /usr/lib/x86_64-linux-gnu/libboost_system.so.1.71.0 /usr/lib/x86_64-linux-gnu/libboost_thread.so.1.71.0 /usr/lib/x86_64-linux-gnu/libPocoFoundation.so.62 -lpthread -ldl -lrt /usr/lib/x86_64-linux-gnu/libpcre.so /usr/lib/x86_64-linux-gnu/libz.so /usr/lib/x86_64-linux-gnu/libboost_atomic.so.1.71.0 -pthread

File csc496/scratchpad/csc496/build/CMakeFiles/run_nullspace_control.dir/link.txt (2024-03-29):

/usr/bin/c++     CMakeFiles/run_nullspace_control.dir/runners/nullspace_control.cpp.o  -o run_nullspace_control   -L/usr/local/include  -Wl,-rpath,/usr/local/include:/usr/local/lib /usr/local/lib/libfranka.so.0.9.2

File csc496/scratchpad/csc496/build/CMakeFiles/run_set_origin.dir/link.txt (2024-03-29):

/usr/bin/c++     CMakeFiles/run_set_origin.dir/runners/set_origin.cpp.o CMakeFiles/run_set_origin.dir/src/common.cpp.o CMakeFiles/run_set_origin.dir/src/ik.cpp.o CMakeFiles/run_set_origin.dir/src/teleop/follower.cpp.o CMakeFiles/run_set_origin.dir/src/teleop/leader.cpp.o CMakeFiles/run_set_origin.dir/src/teleop/network_client.cpp.o CMakeFiles/run_set_origin.dir/src/teleop/network_server.cpp.o  -o run_set_origin   -L/usr/local/include  -Wl,-rpath,/usr/local/include:/usr/local/lib /usr/local/lib/libfranka.so.0.9.2 /usr/lib/x86_64-linux-gnu/libboost_system.so.1.71.0 /usr/lib/x86_64-linux-gnu/libboost_thread.so.1.71.0 /usr/lib/x86_64-linux-gnu/libPocoFoundation.so.62 -lpthread -ldl -lrt /usr/lib/x86_64-linux-gnu/libpcre.so /usr/lib/x86_64-linux-gnu/libz.so /usr/lib/x86_64-linux-gnu/libboost_atomic.so.1.71.0 -pthread

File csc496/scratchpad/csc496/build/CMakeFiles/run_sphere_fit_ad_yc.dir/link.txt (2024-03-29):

/usr/bin/c++     CMakeFiles/run_sphere_fit_ad_yc.dir/runners/sphere_fit_ad_yc.cpp.o CMakeFiles/run_sphere_fit_ad_yc.dir/src/common.cpp.o CMakeFiles/run_sphere_fit_ad_yc.dir/src/ik.cpp.o CMakeFiles/run_sphere_fit_ad_yc.dir/src/teleop/follower.cpp.o CMakeFiles/run_sphere_fit_ad_yc.dir/src/teleop/leader.cpp.o CMakeFiles/run_sphere_fit_ad_yc.dir/src/teleop/network_client.cpp.o CMakeFiles/run_sphere_fit_ad_yc.dir/src/teleop/network_server.cpp.o  -o run_sphere_fit_ad_yc   -L/usr/local/include  -Wl,-rpath,/usr/local/include:/usr/local/lib /usr/local/lib/libfranka.so.0.9.2 /usr/lib/x86_64-linux-gnu/libboost_system.so.1.71.0 /usr/lib/x86_64-linux-gnu/libboost_thread.so.1.71.0 /usr/lib/x86_64-linux-gnu/libPocoFoundation.so.62 -lpthread -ldl -lrt /usr/lib/x86_64-linux-gnu/libpcre.so /usr/lib/x86_64-linux-gnu/libz.so /usr/lib/x86_64-linux-gnu/libboost_atomic.so.1.71.0 -pthread

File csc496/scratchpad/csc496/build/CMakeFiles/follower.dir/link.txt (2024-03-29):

/usr/bin/ar qc libfollower.a  CMakeFiles/follower.dir/src/teleop/follower.cpp.o
/usr/bin/ranlib libfollower.a

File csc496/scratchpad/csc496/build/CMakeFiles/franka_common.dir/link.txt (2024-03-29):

/usr/bin/ar qc libfranka_common.a  CMakeFiles/franka_common.dir/src/common.cpp.o
/usr/bin/ranlib libfranka_common.a

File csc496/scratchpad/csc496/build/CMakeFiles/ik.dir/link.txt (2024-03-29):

/usr/bin/ar qc libik.a  CMakeFiles/ik.dir/src/ik.cpp.o
/usr/bin/ranlib libik.a

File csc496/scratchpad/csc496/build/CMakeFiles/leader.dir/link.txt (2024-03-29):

/usr/bin/ar qc libleader.a  CMakeFiles/leader.dir/src/teleop/leader.cpp.o
/usr/bin/ranlib libleader.a

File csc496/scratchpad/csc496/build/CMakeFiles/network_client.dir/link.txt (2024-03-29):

/usr/bin/ar qc libnetwork_client.a  CMakeFiles/network_client.dir/src/teleop/network_client.cpp.o
/usr/bin/ranlib libnetwork_client.a

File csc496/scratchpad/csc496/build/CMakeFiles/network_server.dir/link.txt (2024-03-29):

/usr/bin/ar qc libnetwork_server.a  CMakeFiles/network_server.dir/src/teleop/network_server.cpp.o
/usr/bin/ranlib libnetwork_server.a

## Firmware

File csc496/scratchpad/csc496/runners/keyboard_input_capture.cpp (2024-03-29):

// Copyright (c) 2017 Franka Emika GmbH
// Use of this source code is governed by the Apache-2.0 license, see LICENSE



#include <iostream>

#include "examples_common.h"
#include "ik.h"
#include <Eigen/Dense>
#include <atomic>
#include <chrono>
#include <cmath>
#include <cstdlib>
#include <eigen3/Eigen/Dense>
#include <franka/exception.h>
#include <franka/robot.h>
#include <fstream>
#include <iomanip>
#include <ncurses.h>
#include <sstream>
#include <thread>
#include <unistd.h>
#include <vector>
std::string CAPTURE_FILE = "capture_location.txt";
double TRAY_WIDTH;
double TRAY_HEIGHT;

namespace robotContext {
franka::Robot *robot;
franka::Gripper *gripper;
franka::Model *model;

} // namespace robotContext

namespace global_variable {
std::array<double, 16> current_ee_pose;
bool flag_done_collecting;
std::vector<std::array<double, 16>> collected_ee_poses;
} // namespace global_variable

std::atomic<bool> captureRequested(false);
std::atomic<bool> stopKeyPressThread(false);
std::atomic<bool> moveForward(false);
std::atomic<bool> moveBackward(false);
std::atomic<bool> moveLeft(false);
std::atomic<bool> moveRight(false);
std::atomic<bool> moveUp(false);
std::atomic<bool> moveDown(false);
std::atomic<bool> rotateClockwise(false);
std::atomic<bool> rotateCounterClockwise(false);
const double MIN_ROTATION = 0;      // Example min rotation in radians
const double MAX_ROTATION = M_PI_2; // Example max rotation in radians
const double ROTATION_STEP = (M_PI / 180.0) * 10;

template <typename T>
T getInputWithinBounds(const T lowerBound, const T upperBound,
                       const std::string &prompt) {
  T inputValue;
  while (true) {
    std::cout << prompt;
    std::cin >> inputValue;
    if (std::cin.fail() || inputValue < lowerBound || inputValue > upperBound) {
      std::cin.clear(); // Clear the error flag
      std::cin.ignore(std::numeric_limits<std::streamsize>::max(),
                      '\n'); // Discard the input
      std::cout << "Input must be between " << lowerBound << " and "
                << upperBound << ". Please try again.\n";
    } else {
      break; // Input is within bounds, exit the loop
    }
  }
  return inputValue;
}

void open_gripper() {
  if (robotContext::gripper) {
    robotContext::gripper->grasp(0.06, 0.08,
                                 30);
  }
}

void close_gripper() {
  if (robotContext::gripper) {
    robotContext::gripper->grasp(0.01, 0.08,
                                 30); 
  }
}


void listenForKeyPress() {
  initscr();             // Initialize ncurses mode
  cbreak();              // Disable line buffering
  noecho();              // Don't echo pressed keys to the console
  nodelay(stdscr, TRUE); // Non-blocking getch

  int ch;
  while (!stopKeyPressThread.load()) { // Check the flag
    ch = getch();                      // Get character

    switch (ch) {
    case ' ':
      captureRequested.store(true);
      break;
    case 's':
      moveForward.store(true);
      break;
    case 'w':
      moveBackward.store(true);
      break;
    case 'a':
      moveLeft.store(true);
      break;
    case 'd':
      moveRight.store(true);
      break;
    case 'r':
      moveUp.store(true);
      break;
    case 'f':
      moveDown.store(true);
      break;
    case 'g': // Grasp (close) the gripper
      close_gripper();
      break;
    case 't': // Release (open) the gripper
      open_gripper();
      break;
    case 'j': // rotate counter-clockwise
      rotateCounterClockwise.store(true);
      break;
    case 'k': // rotate clockwise
      rotateClockwise.store(true);
      break;
    case 27:
      stopKeyPressThread.store(true);
      break;
    default:
      break;
    }
    std::this_thread::sleep_for(
        std::chrono::milliseconds(100)); // Reduce CPU usage
  }

  endwin(); // End ncurses mode
}


void set_location(double x_OTEE, double y_OTEE, double z_OTEE) {
  double x_offset = 0, y_offset = 0, z_offset = 0.1;
  double x_desired = x_OTEE + x_offset;
  double y_desired = y_OTEE + y_offset;
  double z_desired = z_OTEE + z_offset;

  double k = 0.01;
  Eigen::Matrix4d transformation;
  Eigen::Matrix4d current_pose;

  std::cout << "Setting location to (" << x_desired << ", " << y_desired << ", "
            << z_desired << ")" << std::endl;

  // store eigen matrix in c array
  std::array<double, 16> result_array = {
    0, 1, 0, 0,
    -1, 0, 0, 0,
    0, 0, -1, 0,
    x_desired, y_desired, z_desired, 1
  };

    global_variable::current_ee_pose = result_array;
  global_variable::flag_done_collecting = true;
}

double distance(const Eigen::Vector3d &v1, const Eigen::Vector3d &v2) {
  Eigen::Vector3d diff = v1 - v2;
  return diff.norm();
}


int main(int argc, char **argv) {
  std::vector<std::array<double, 16>> ee_poses;
  if (argc != 5) {
    std::cerr << "Usage: " << argv[0] << " <robot-hostname> <x> <y> <z>" << std::endl;
    return -1;
  }
  global_variable::flag_done_collecting = false;

  franka::Robot robot(argv[1]);
  robotContext::gripper = new franka::Gripper(argv[1]);
  double x = 0.0, y=0.0, z=0.0;

  try {
    // Parse x, y, and z values from command line arguments
    x = std::stod(argv[2]);
    y = std::stod(argv[3]);
    z = std::stod(argv[4]);


  } catch (const std::invalid_argument &e) {
    std::cerr << "Invalid number: " << e.what() << std::endl;
    return 1;
  } catch (const std::out_of_range &e) {
    std::cerr << "Number out of range: " << e.what() << std::endl;
    return 1;
  }

  InverseKinematics ik_controller(1, IKType::M_P_PSEUDO_INVERSE);
  int point = 1;
  char input;
  robotContext::robot = &robot;
  franka::RobotState state;
  franka::Model model = robot.loadModel();
  robotContext::model = &model;
  int choice{};

  // Set sweeping origin
  set_location(x, y, z);

  Eigen::Matrix4d pose =
      Eigen::Matrix4d::Map(global_variable::current_ee_pose.data());
  double time = 0.0;
  int phase = 0;              // Current phase of the rectangle sweep
  double phase_start_time = 0.0;
  double phase_length = 3;
  double initial_y = pose(1, 3);
  bool isCaptured = false;


  std::cout<< "To capture the position of the object, move the robot with keyboard inputs. Here are the key mappings:\n"
  "w: forwards \n"
  "s: backwards \n"
  "a: left \n"
  "d: right \n"
  "r: up \n"
  "f: down \n"
  "SPACEBAR: capture object location (don't get too close, the height does not matter)\n"
  "ESC: quit object capturing\n"
  "\n Make sure probe is directly above object when capturing, press enter to continue ...\n"
            << std::endl;
  std::cin.ignore();

  std::thread keyPressThread(listenForKeyPress);

  robot.control([&time, &pose, &ik_controller, &phase,
                 &phase_start_time, &phase_length, &initial_y, &isCaptured](
                    const franka::RobotState &robot_state,
                    franka::Duration period) -> franka::JointVelocities {
    time += period.toSec();
    double move_step = 0.005;

    if (moveForward.load()) {
      pose(0, 3) += move_step; // Move forward
      moveForward.store(false);
    } else if (moveBackward.load()) {
      pose(0, 3) -= move_step; // Move backward
      moveBackward.store(false);
    } else if (moveLeft.load()) {
      pose(1, 3) -= move_step; // Move left
      moveLeft.store(false);
    } else if (moveRight.load()) {
      pose(1, 3) += move_step; // Move right
      moveRight.store(false);
    } else if (moveDown.load()) {
      pose(2, 3) -= move_step; // Move downs
      moveDown.store(false);
    } else if (moveUp.load()) {
      pose(2, 3) += move_step; // Move up
      moveUp.store(false);
    } else if (rotateCounterClockwise.load()) {
      Eigen::Matrix3d rotationMatrix =
          Eigen::AngleAxisd(ROTATION_STEP, Eigen::Vector3d::UnitZ())
              .toRotationMatrix();
      Eigen::Matrix4d poseMatrix = Eigen::Matrix4d::Map(pose.data());
      Eigen::Matrix3d currentRotation = poseMatrix.block<3, 3>(0, 0);
      Eigen::Matrix3d newRotation = rotationMatrix * currentRotation;
      poseMatrix.block<3, 3>(0, 0) = newRotation;
      Eigen::Map<Eigen::Matrix<double, 16, 1>>(pose.data()) =
          Eigen::Matrix<double, 16, 1>::Map(poseMatrix.data(), 16);
      rotateCounterClockwise.store(false);
    } else if (rotateClockwise.load()) {
      Eigen::Matrix3d rotationMatrix =
          Eigen::AngleAxisd(-ROTATION_STEP, Eigen::Vector3d::UnitZ())
              .toRotationMatrix();
      Eigen::Matrix4d poseMatrix = Eigen::Matrix4d::Map(pose.data());
      Eigen::Matrix3d currentRotation = poseMatrix.block<3, 3>(0, 0);
      Eigen::Matrix3d newRotation = rotationMatrix * currentRotation;
      poseMatrix.block<3, 3>(0, 0) = newRotation;
      Eigen::Map<Eigen::Matrix<double, 16, 1>>(pose.data()) =
          Eigen::Matrix<double, 16, 1>::Map(poseMatrix.data(), 16);
      rotateClockwise.store(false);
    }

    // Check if capture was requested
    if (captureRequested.load() && !isCaptured) {
      // Capture current XYZ coordinates
      Eigen::Vector3d current_position(robot_state.O_T_EE[12],
                                       robot_state.O_T_EE[13],
                                       robot_state.O_T_EE[14]);
      std::cout << "Captured Position: " << current_position.transpose()
                << std::endl;
      std::cout << "Time: " << time << std::endl;

      // Open file and append the captured position
      std::ofstream outFile;
      outFile.open(CAPTURE_FILE, std::ios::out); // Open in write mode
      outFile << pose(12) << " " << pose(13) << " " << pose(14) << std::endl;
      outFile.close();

      // Reset the request flag
      captureRequested.store(false);
      isCaptured = true;
    }

    franka::JointVelocities output_velocities =
        ik_controller(robot_state, period, pose);
    Eigen::Map<const Eigen::Matrix<double, 7, 1>> output_eigen_velocities(
        robot_state.dq.data());
    Eigen::Vector3d current_position(
        robot_state.O_T_EE[12], robot_state.O_T_EE[13], robot_state.O_T_EE[14]);
    Eigen::Vector3d desired_position(pose(0, 3), pose(1, 3), pose(2, 3));
    double dist = distance(current_position, desired_position);

    if (stopKeyPressThread.load()) {
      output_velocities = {0.0, 0.0, 0.0, 0.0, 0.0, 0.0, 0.0};
      return franka::MotionFinished(output_velocities);
    }
    return output_velocities;
  });

  stopKeyPressThread.store(true); // Signal the thread to stop
  keyPressThread.join();          // Wait for the thread to finish

  return 0;
}

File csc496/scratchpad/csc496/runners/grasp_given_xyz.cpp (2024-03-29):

// Copyright (c) 2017 Franka Emika GmbH
// Use of this source code is governed by the Apache-2.0 license, see LICENSE

#include <iostream>

#include "ik.h"
#include <Eigen/Dense>
#include <chrono>
#include <cmath>
#include <eigen3/Eigen/Dense>
#include <franka/exception.h>
#include <franka/robot.h>
#include <limits>
#include <thread>
#include <vector>

#include "examples_common.h"
double Z_BOARD = -0.001; // Board height constant

namespace robotContext {
franka::Robot *robot;
franka::Gripper *gripper;
franka::Model *model;

} // namespace robotContext

namespace global_variable {
std::array<double, 16> current_ee_pose;
bool flag_done_collecting;
std::vector<std::array<double, 16>> collected_ee_poses;
} // namespace global_variable

template <typename T>
T getInputWithinBounds(const T lowerBound, const T upperBound,
                       const std::string &prompt) {
  T inputValue;
  while (true) {
    std::cout << prompt;
    std::cin >> inputValue;
    if (std::cin.fail() || inputValue < lowerBound || inputValue > upperBound) {
      std::cin.clear(); // Clear the error flag
      std::cin.ignore(std::numeric_limits<std::streamsize>::max(),
                      '\n'); // Discard the input
      std::cout << "Input must be between " << lowerBound << " and "
                << upperBound << ". Please try again.\n";
    } else {
      break; // Input is within bounds, exit the loop
    }
  }
  return inputValue;
}

void open_gripper() {
  if (robotContext::gripper) {
    robotContext::gripper->move(0.06, 0.08);
  }
}

void close_gripper() {
  if (robotContext::gripper) {
    robotContext::gripper->grasp(0.01, 0.08, 30);
  }
}

// set target location for watching and gripping an object
void set_location(double x_raw, double y_raw) {
  double x_offset = 0.06, y_offset = 0, z_offset = 0.1;
  double x_desired = x_raw + x_offset;
  double y_desired = y_raw + y_offset;
  double z_high = Z_BOARD + z_offset;

  std::cout << "Watch object pose set as: (" << x_desired << ", " << y_desired
            << ", " << z_high << ")" << std::endl;

  std::array<double, 16> pose_watch_object = {
      0, 1, 0, 0, -1, 0, 0, 0, 0, 0, -1, 0, x_desired, y_desired, z_high, 1};
  global_variable::collected_ee_poses.push_back(pose_watch_object);

  std::cout << "Grip object pose set as: (" << x_desired << ", " << y_desired
            << ", " << Z_BOARD << ")" << std::endl;

  std::array<double, 16> pose_grip_object = {
      0, 1, 0, 0, -1, 0, 0, 0, 0, 0, -1, 0, x_desired, y_desired, Z_BOARD, 1};
  global_variable::collected_ee_poses.push_back(pose_grip_object);
  global_variable::flag_done_collecting = true;
}

double distance(const Eigen::Vector3d &v1, const Eigen::Vector3d &v2) {
  Eigen::Vector3d diff = v1 - v2;
  return diff.norm();
}

int main(int argc, char **argv) {
  // Ensure correct command line arguments are provided
  if (argc != 5) {
    std::cerr << "Usage: " << argv[0] << " <robot-hostname> <x> <y> <z>"
              << std::endl;
    return -1;
  }

  global_variable::flag_done_collecting = false;
  // Initialize the robot and gripper with the provided hostname
  franka::Robot robot(argv[1]);
  robotContext::gripper = new franka::Gripper(argv[1]);

  double x = 0.0, y = 0.0, z = 0.0;

  try {
    // Parse x, y, and z values from command line arguments
    x = std::stod(argv[2]);
    y = std::stod(argv[3]);
    z = std::stod(argv[4]);

  } catch (const std::invalid_argument &e) {
    std::cerr << "Invalid number: " << e.what() << std::endl;
    return 1;
  } catch (const std::out_of_range &e) {
    std::cerr << "Number out of range: " << e.what() << std::endl;
    return 1;
  }

  std::vector<std::array<double, 16>> ee_poses;

  // Home robot and prompt user to remove probe
  setDefaultBehavior(robot);
  std::array<double, 7> q_goal = {
      {0, 0, 0, -3 * M_PI_4, 0, 3 * M_PI_4, M_PI_4}};
  MotionGenerator motion_generator(0.15, q_goal);
  std::cout << "Please remove the probe. \nThe robot will then move to the "
               "homing position press Enter "
               "to continue..."
            << std::endl;
  std::cin.ignore();
  robot.control(motion_generator);

  InverseKinematics ik_controller(1, IKType::M_P_PSEUDO_INVERSE);
  int point = 1;
  char input;
  robotContext::robot = &robot;
  franka::Model model = robot.loadModel();
  robotContext::model = &model;

  // Prompt user for voxel values
  set_location(x, y);
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

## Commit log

2024-03-27 added stl files
    [Franka_gripper.stl, Franka_gripper_softjaw.stl, Franka_probe_clamp.stl, Franka_probe_clamp_softjaw.stl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]
2024-03-27 added printing and assembly instructions
2024-03-27 fixed printing and assrmbly instructions
2024-03-28 added and fixed printing and assembly pdf
2024-03-29 Updated assembly and printing instructions pdf
